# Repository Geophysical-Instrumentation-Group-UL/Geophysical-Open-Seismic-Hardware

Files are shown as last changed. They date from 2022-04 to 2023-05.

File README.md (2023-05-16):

# Geophysical Open Seismic Hardware

The Geophysical Open Seismic Hardware initiative is brought to you by the Geophysical Instrumentation Group at Université Laval (GIGul) and is funded by the Fonds de Recherche du Québec- Nature et technologies (FRQNT). This open-hardware contribution provides Earth Scientists around the world with a reference design for multi-component borehole seismic array that can be deployed from a conventional wireline winch used in the mineral industry (1/8 single conductor armoured cable). This design is engineered around the Teensy 4.0 microcontroller board which is compatible with the Arduino ecosystem and will be familiar to engineers and tinkerers. Our design philosophy is to include easily sourced components as part of modules that can readily be modified for other geophysical acquisition projects.

This repository contains all the design files for the different printed circuit boards that are integrated in this modular design(PCB). The first module includes a 3 channel 24 bit ADC that can sample signals up to 32 kHz. The second module is a power supply module that is configured to condition the power used by downhole shuttle. We provide a KiCad version of these design files. In early 2022, we migrated the project from Altium to KiCad in order to meet the ethos of our project and allow more users to benefit from our developments. Here are images of the V2 prototype WorkerBoard as assembled in december 2022. 

 Details about specific aspects of the project can be found on in the doc repository. For more information and questions please contact arnaud.mercier05@gmail.com or christian.dupuis@ggl.ulaval.ca.

 The hardware development is under the TAPR Open Hardware License, while the firmware is under the GNU General Public License V3. License files are within respective directory.

Addition of November 2022 : 
A basic GUI is now available. This first version allows the user to configure and control the system with 3 shuttles. It also have a display window to anayse the individual shots as well as the stacked trace.

The article titled ``Geophysical Open Seismic Hardware: Design of a Vertical Seismic Profiling Instrument'' documents the performance and the first field validation of the prototype : https://openhardware.metajnl.com/articles/10.5334/joh.50

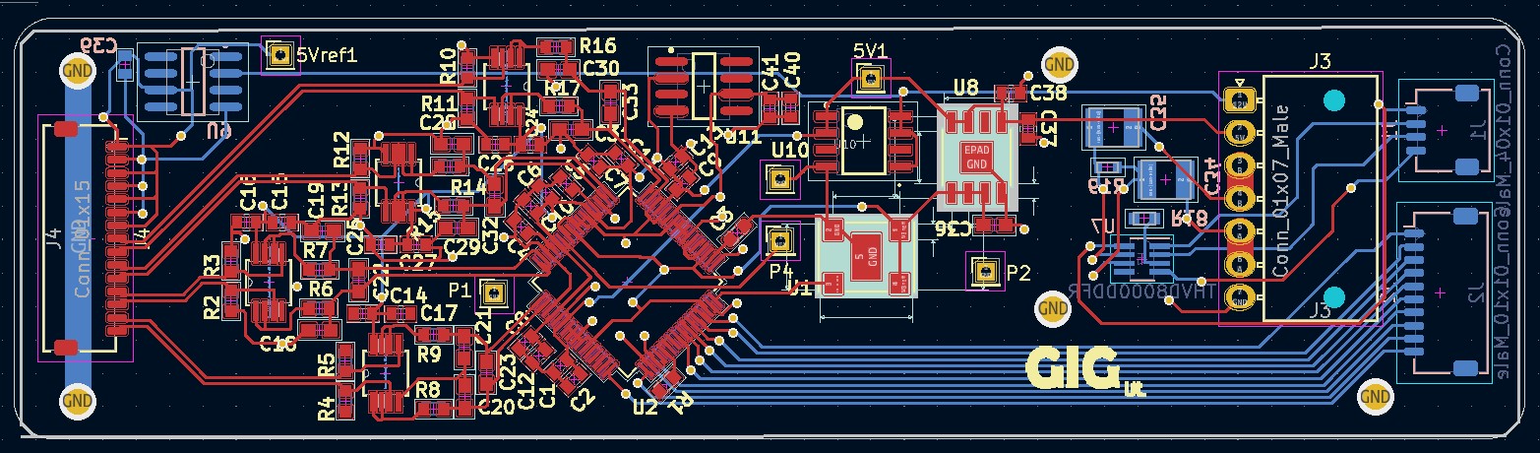
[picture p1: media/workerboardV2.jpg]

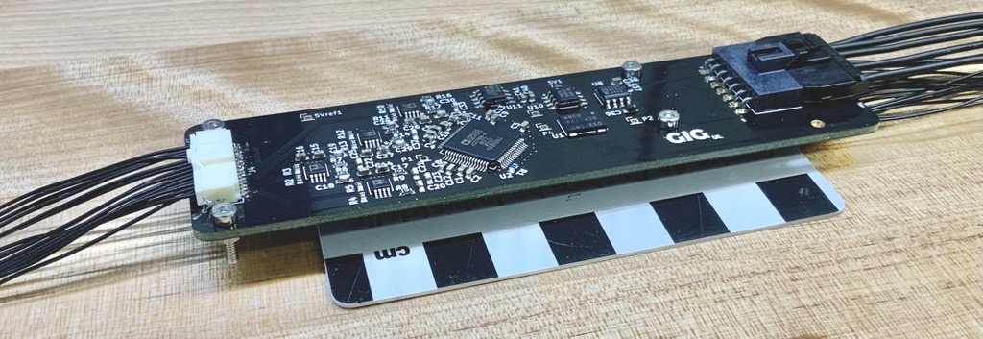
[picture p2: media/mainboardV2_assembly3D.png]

GUI

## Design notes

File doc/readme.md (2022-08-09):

GiGUL

# Welcome to the Geophysical Open Seismic Hardware documentation!
In this directory you will find details about the Geophysical Open Seismic Hardware project goals, design guidelines, assembly instruction and current stage of development. This repo is hosting the modifiable hardware files, assembly instruction and software required to operate the tools.

# What

 The Geophysical Open Seismic Hardware initiative is to design an open source VSP tool that is modular and can be reused or adapted by other research group for their purposes.  This contribution presents our first geophysical open-hardware contribution. We have developed a rugged and versatile 24-bit geophysical logger. The control and synchronization of the acquisition system is engineered around Arduino compatible microcontrollers that are open-source. This provides an intuitive and vibrant development community. A frequency modulated communication protocol allows us to communicate data efficiently and send power over a single conductor wireline. This modular geophysical logger can easily be reconfigured to be used with multiple sensors. The first use case of this logger is a Vertical Seismic Profiling tool chain. The novel design reduces the overall cost and size, which facilitates the deployment of more channels and in configurations that are not feasible with current commercial equipment. In particular the system in composed of :

- Analog accelerometer from Silicon Design (SI1521L)
- AD7768 multi-channel Delta-Sigma 24 bits ADC
- THVD8000 Frequency modulated RS-485
- Teensy 4.0 MC

# Overview

The system is based on a leader/worker arrangement. The leader (master) unit uphole is connected directly via USB to the PC. This leader unit is the same as the worker unit without the power supply and sensor modules. There are multiple Workers (shuttles) but only one leader uphole. DC voltage is applied on the A and B line which is used to power up the worker units. Each worker is in a pressure housing to be able to sustain borehole conditions. At the time being, the pressure housing is still in development.

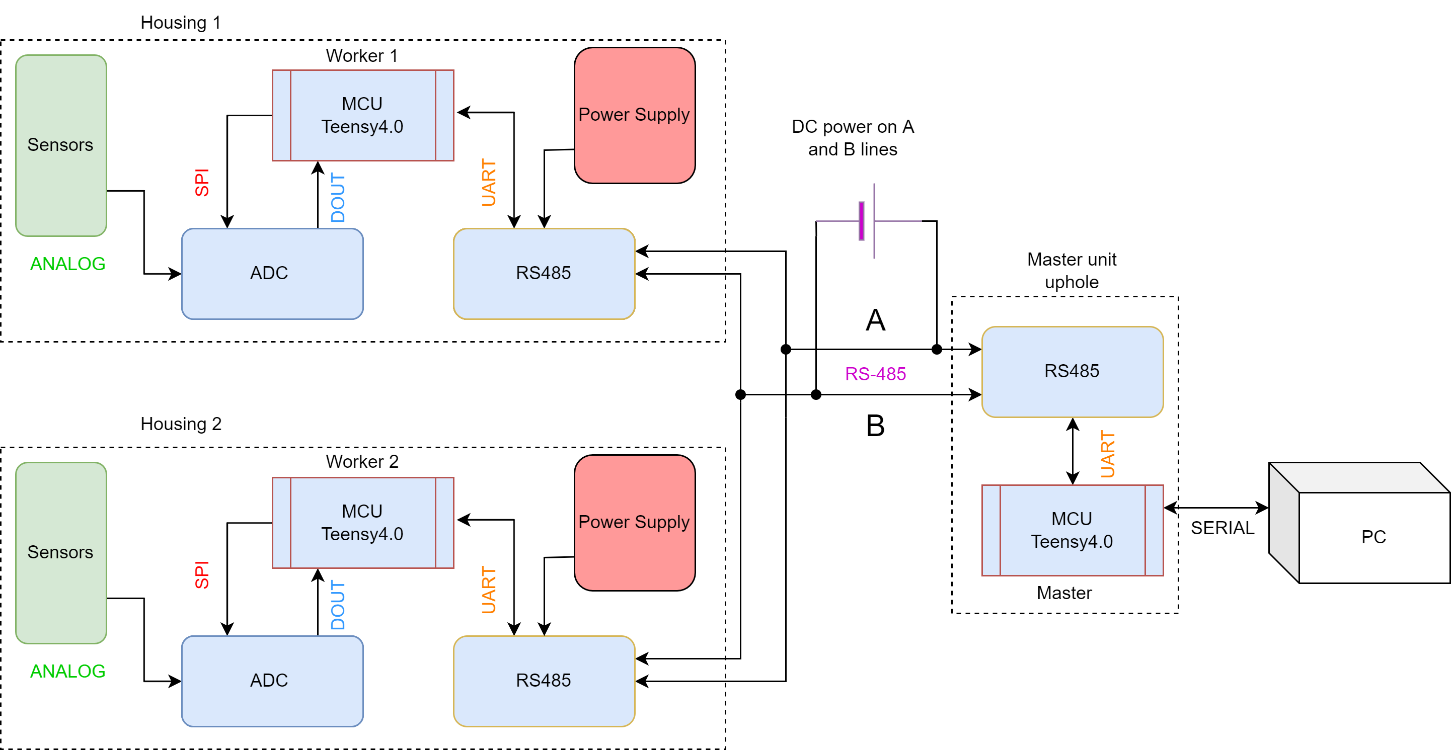
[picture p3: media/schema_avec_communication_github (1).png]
Scheme


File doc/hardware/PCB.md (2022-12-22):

# Printed circuit board details

----

## Main board (ADC_RS)

The components have been divided on 3 different printed circuit boards (PCB). The main board contains the ADC, the MCU and the communication module. This board has 4 layers in order to reduce its size as much as possible and to ensure a decoupling between the digital signals, the analog signals and the power supply. Its dimensions of 40 by 160 mm respects the objective of a diameter less than 46 mm. The Altium version contains micro-vias, which is more costly to produce. This version is deprecated and is present here only for reference. The active board is the KiCad version, which doesn't have micro-vias.

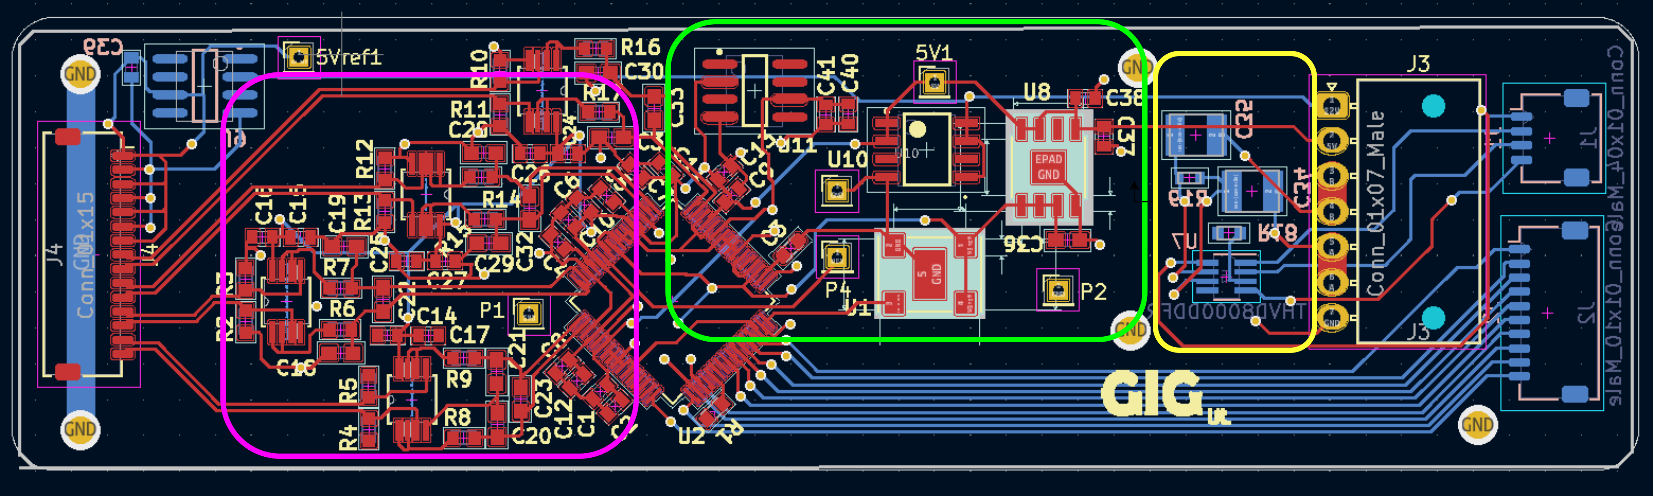
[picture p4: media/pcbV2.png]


### ADC drivers (pink)

Those are 2 channels amplifiers with unity gain to drive the ADC analog inputs. They are ADA4841-2 from Analog Device. The output of a sensor has 2 signals. Both signal are conditioned by an amplifier before going to the ADC. The design of this amplification stage is based on the application note https://www.analog.com/media/en/technical-documentation/application-notes/AN-1384.pdf.

### Voltage regulator (green)

4 different voltage regulator are used on this board. The 4.096 V is used as a reference for the ADC. The 3.3 power up the clock and reference the ADC. The 5Vref is the reference for the sensors and it is a high precision voltage regulator while the 5V is used to power up the ADC and other component, he can produce higher current than the 5Vref. 

### RS-485 (Yellow)

The THVD8000 is responsible of transforming the UART data to a frequency modulated RS-485 signal that is send on the A and B line. The carrier frequency is set by the R22 resistors. Values of resistor can be found in the THVD8000 [datasheet](https://www.ti.com/product/THVD8000?utm_source=google&utm_medium=cpc&utm_campaign=asc-int-null-prodfolderdynamic-cpc-pf-google-wwe&utm_content=prodfolddynamic&ds_k=DYNAMIC+SEARCH+ADS&DCM=yes&gclid=Cj0KCQjwof6WBhD4ARIsAOi65ajVA_-4Qv5Z8-NflDabHUv2FtYJd0RHMERMfylwqK505uBJHmn_EZ0aAl1MEALw_wcB&gclsrc=aw.ds). The choice of the decoupling capacitor is based on the application note here [THVD8000 design guide](https://www.ti.com/lit/an/slla496a/slla496a.pdf?ts=1658843537116&ref_url=https%253A%252F%252Fwww.ti.com%252Fproduct%252FTHVD8000%253Futm_source%253Dgoogle%2526utm_medium%253Dcpc%2526utm_campaign%253Dasc-int-null-prodfolderdynamic-cpc-pf-google-wwe%2526utm_content%253Dprodfolddynamic%2526ds_k%253DDYNAMIC%2BSEARCH%2BADS%2526DCM%253Dyes%2526gclid%253DCj0KCQjwof6WBhD4ARIsAOi65ajVA_-4Qv5Z8-NflDabHUv2FtYJd0RHMERMfylwqK505uBJHmn_EZ0aAl1MEALw_wcB%2526gclsrc%253Daw.ds).

### Connectors 

J1 is dedicated to the communication chip. Theses wire have to be connected to the chosen MCU. J2 is a 10 pin connector dedicated to the configuration and communication with the ADC. J3 is a 7 pin high power connector used by the A,B and 12V lines. Finally, the J4 15 pin connector is used to drive and collect the signals from 4 analog differential sensors.

## Power supply

The power supply and its component are built into a separate 40 by 85 mm PCB. This way, switching noise cannot affect the precision components of the main board. The design is based on the [DC2895A](https://www.analog.com/en/design-center/evaluation-hardware-and-software/evaluation-boards-kits/dc2895a.html#eb-overview) demo board. On one side the A and B line enters and goes thru the inductor to filter out the high frequency.  Since the cable is expected to have a high capacitance (140 microF), turning on the power supply can create a  current surge. The added 100 Ohms resistor (R5) allows to reduce the current spike when turning on the power supply. The mode header is used to set the operating mode for the output of the power supply. Burst mode is the default since it draws less current.

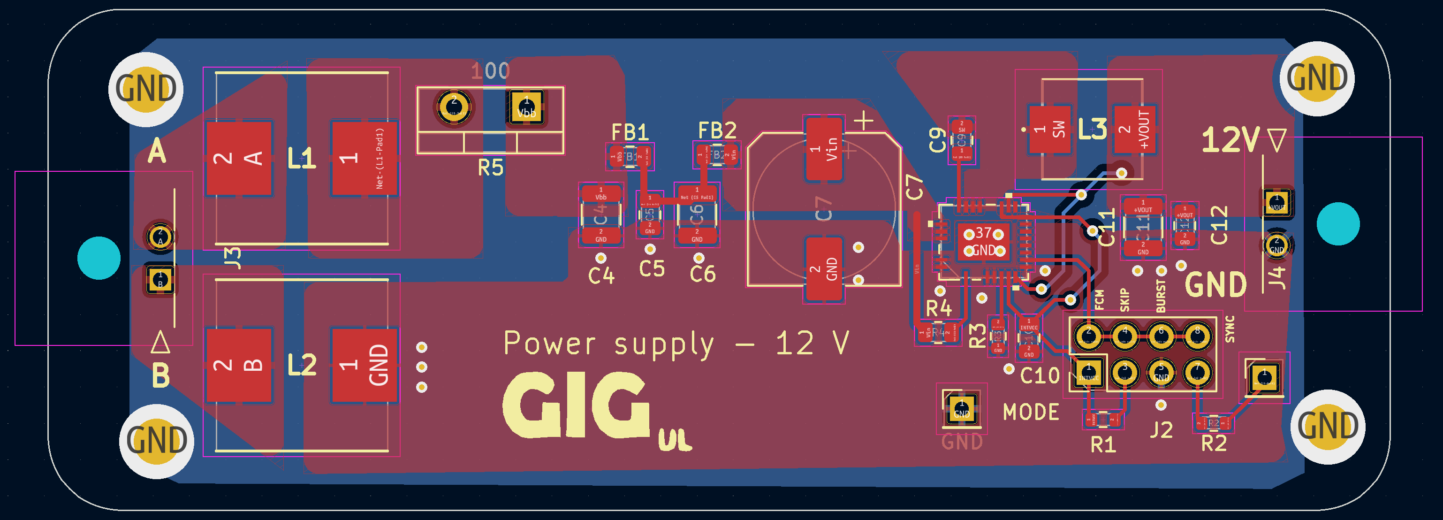
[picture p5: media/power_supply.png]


## Sensors

The sensors are assembled on miniature PCBs in order to facilitate the assembly on a mount with the desired geometry.  Wires are soldered directly into the sensor boards. These wires are linked to the main board by a locking clip connector to ensure proper contact The PCB follows the connection proposed in the sensor datasheet ([si1521L](https://www.silicondesigns.com/_files/ugd/3fcdcf_d6eb801b372f408bbba8180fd1f07cc7.pdf)). 

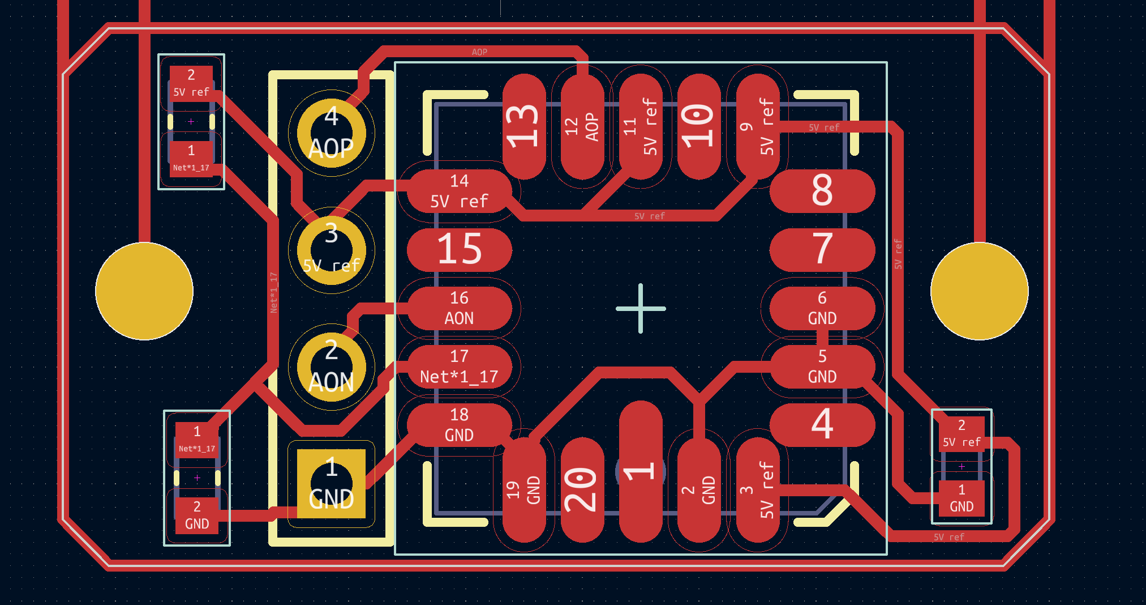
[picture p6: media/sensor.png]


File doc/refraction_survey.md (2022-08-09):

# Refraction survey

---

Here is the details about the refraction survey from the article. All the 3D files have been developed in CREO and are available in the 3D_files directory.

## Goals

- Compare our system with the well proven *Geode* from geometrics (first arrivals and complete seismograph)
- Test the custom 3 components sensor package

## Integration of the electronics

### Sensor package

The SI 1521L are soldered on the sensor board and jumper wires are soldered to the PCB. A 3D printed box with tapered insert allow to fix the PCB in an orthogonal arrangement. Every board are connected to a wall mount DB15 connector.

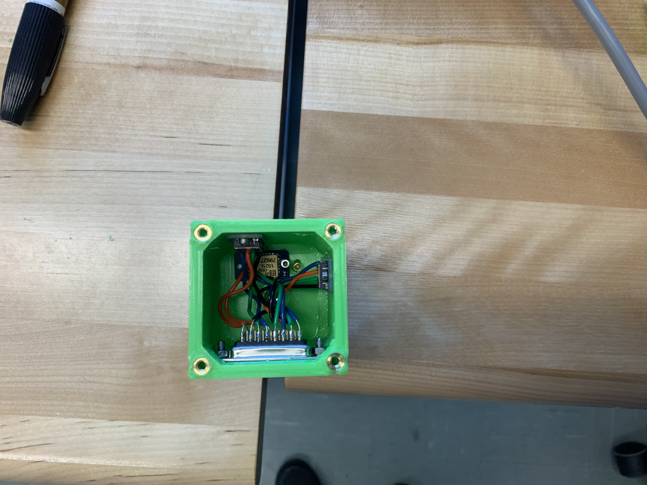
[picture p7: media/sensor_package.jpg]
sensors


### Main board and power supply

The main board and the power supply board were integrated onto an 3D printed frame via screws. On one end of the frame is a custom expander plug mechanism and on the other end a printed TPU (flexible) ring. These allow to slide the frame inside an 2 inch aluminium tube and lock the frame so it doesn't move. A custom cable is assemble based on a DB15 cable. Wires for the sensor package that come from the main board are soldered into the pre-assemble DB15 cable and wrapped around heat-shrink.

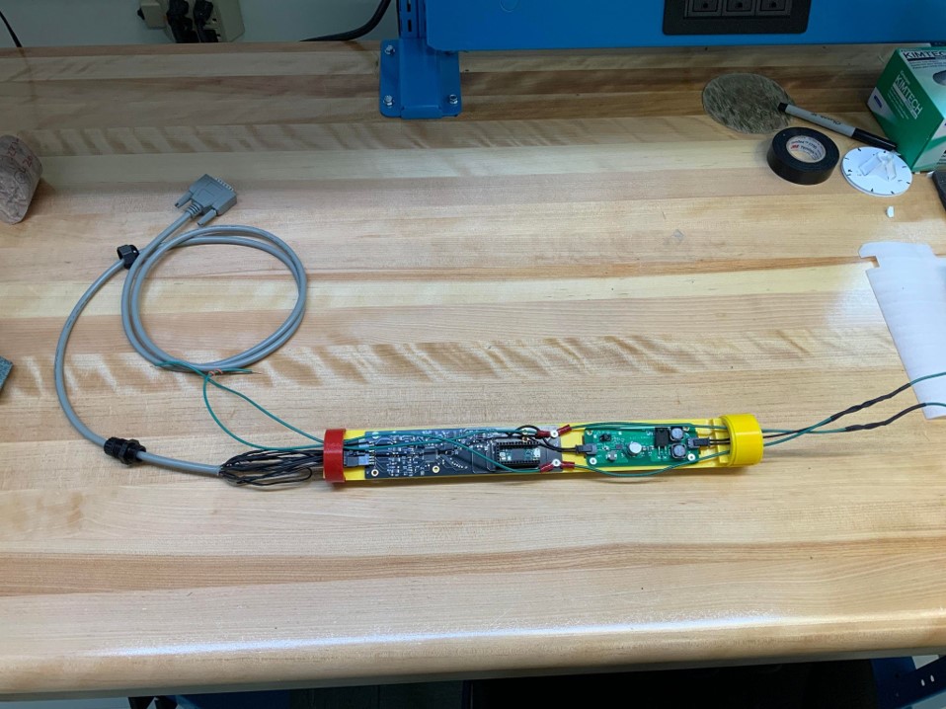
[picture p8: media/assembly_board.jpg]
assembly


### End cap

A custom end cap is designed and 3D printed. This cap has some threaded insert so it can be fix by a screw through the tube wall. These cap have a cavity for a cable gland for the DB15 cable and for the coax wall mount connector.

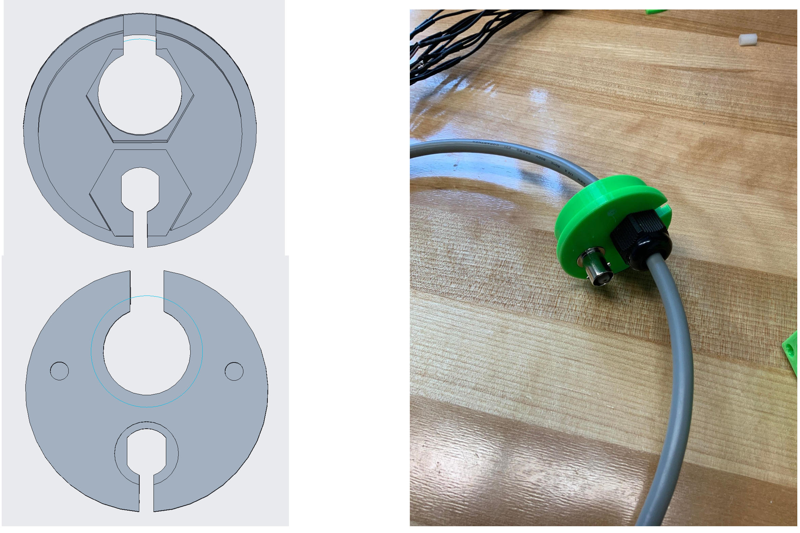
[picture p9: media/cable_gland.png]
gland

coax

### Master box

The master unit is bolted into a simple 3D printed box with a removable cover. The box has a wall mount coax connector and a slid to allow the passage of the USB cable. Banana jack are included to connect the external power supply. Wires for the trigger are accessed from a hole in the box cover.

box

### Custom trigger

A custom trigger system composed of a piezo-electric ([Sparkfun](https://www.sparkfun.com/products/10293)) element is mounted onto a sledgehammer. The mount is 3D printed and is divided in 3 main parts:

- 2 pieces clamp in rigid plastic (CPE)
- 2 half-circle TPU ring that provides damping and reduce stress on the CPE plastic
- 1 TPU top cap to keep the piezo in place

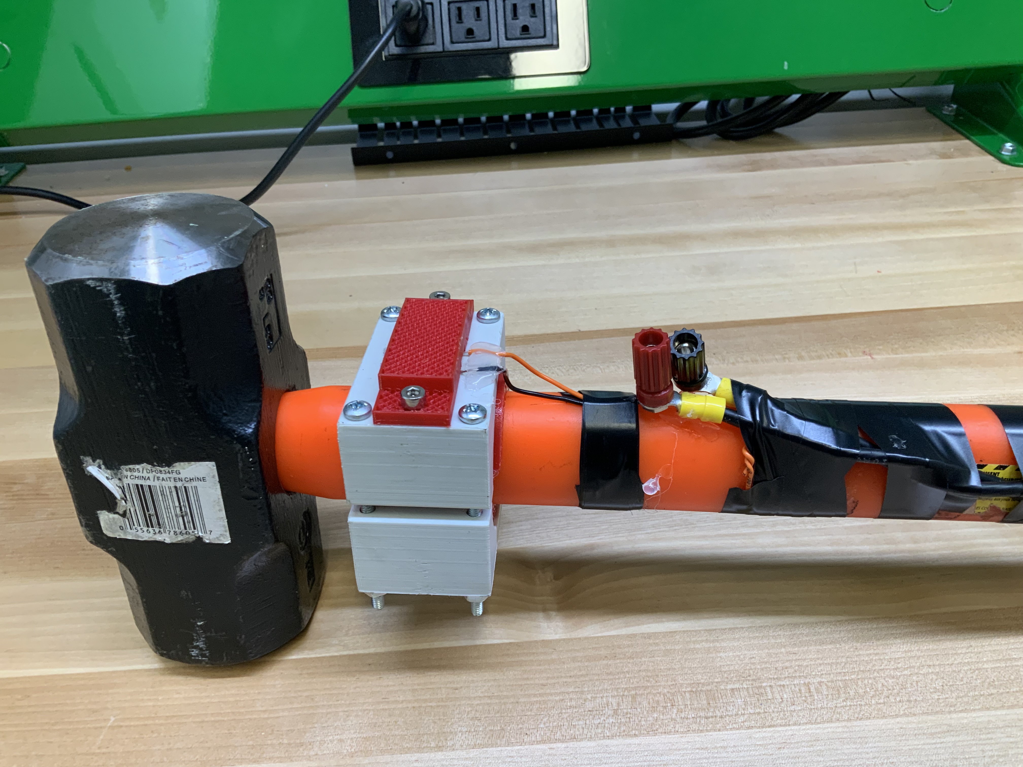
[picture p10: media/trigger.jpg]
trigger


## Material used

- Voltage source (HMP4040 from Rhode and Schwarz)
- Generator to power the voltage source
- Laptop with the custom software for the tool
- Sledgehammer and metal plate
- Measuring tape
- Geode from geometrics and associated cables
- Laptop with proper geometrics software
- 12 V battery
- Geophones (ION 28 Hz)

## Geometry

See images in the article.

## Data

Raw data are stored in .txt files and are available on request.

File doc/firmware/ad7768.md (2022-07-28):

**Homemade librairy to configure ad7768 with Arduino SPI**

This librairy is adapted from the original ad7768 librairy from [Analog device ad7768](https://github.com/analogdevicesinc/no-OS/blob/master/drivers/adc/ad7768/ad7768.c). It implements the same logic but adapted with he Arduino SPI function.

All functions are based on a _ad7768_chip_ object:

    typedef struct {
        ad7768_chip_select_pin chipSelectPin = 10; //teensy 4.0 CS pin
        ad7768_power_mode	power_mode;
        ad7768_mclk_div		mclk_div;
        ad7768_dclk_div		dclk_div;
        ad7768_dec_rate		dec_rate;
        ad7768_filt_type	filt_type;
    } ad7768_chip;

This object contains a list parameters of a type enum. This makes it easier and cleaner when configuring a new chip. For example, in the declaration of a new chip, one can decide to set the power mode to only theses values:

    typedef enum {
        AD7768_ECO = 0,
        AD7768_MEDIAN = 2,
        AD7768_FAST = 3,
    } ad7768_power_mode;

Some functions have a mask input parameter. This allows to write in only a specific part of a registry without changing the already in place values. The function _print_config_ has a stream input parameter. This allows to print the configurations in a specific Serial port. 

A list of the registry address is define in the .h file. Those are taken from the datasheet. This librairy is dependant on the Arduino SPI librairy and Stream librairy only.

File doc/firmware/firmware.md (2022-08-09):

# Firmware

In this page you will find details about the Geophysical Open Seismic Hardware firmware, design guidelines and current stage of development. The details about the librairy used in the projects can be found in the command and ad7768 files.

# Design guidelines

This basic software is the first prototype of the control software. Only the essentials functions are implemented. This software looks at doing 2 things in particular:

- Ease of use and high-level function to operate the system [main.py and mainLeader].
- High-speed acquisition of seismic signal from the ADC (32 kHz) [mainWorker].

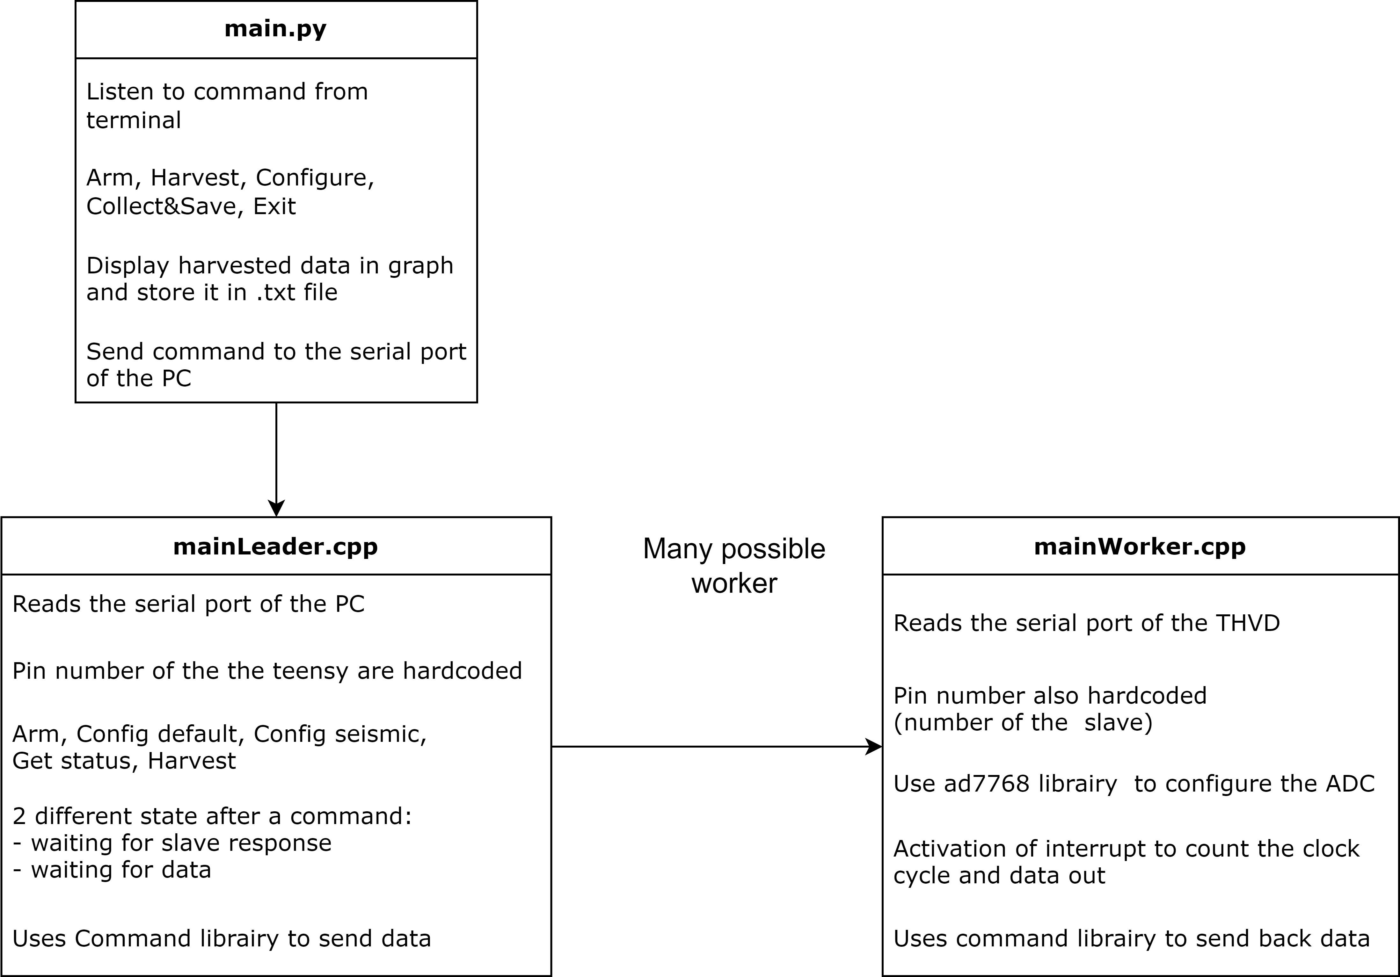
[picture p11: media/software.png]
Software


# Principal elements in main scripts:

## main.py

This script runs on the PC used for the acquisition. It must be launched in the terminal once the leader unit is connect by USB. This script allow the user to enter high level command to perform a basic survey.

- Read the input of the terminal (the serial port and baud rate must be specified, 115200 by default).
- Transform the data from 24 bits to voltage. The values are hardcoded.
- Plot the results of the harvested data (only 3 worker for now).
  The X is the value of the worker you wish to harvest.
- Typical use case:
  - Enter the sampling rate and duration in the terminal.
  - Create a new stack.
  - Use of arm and collect function after each shot (shot count will appear).
  - Use of the show stack function to display individual shots and stacked traces.
  - Create a new stack and carry on.

## mainLeader.cpp

This script runs on the leader MCU (Teensy 4.0). The MCU are programmed from the PlatformIO extension in Visual Studio code.

- Read the serial from PC and read the command (Uses the by default serial port to PC and a specific serial port to the RS485 chip).
 - If the arm command is detect the trigger interrupt is activated.
 - If the trigger is detected, a signal is sent to the workers and the trigerred state is turned off.
- If the harvest data command is detected the flag waitForData is activated.

The script uses the functions of the _command_ librairy to communicate with the workers. When the leader waits for a worker response the function _readCommand_ of the _command_ librairy is used to detect the incoming command type from the worker.

## mainWorker.cpp

This script runs on every worker MCU (Teensy 4.0). The MCU are programmed from the PlatformIO extension in Visual Studio code. Each worker must be assigned a unique workerID. This will allow the leader unit to communicate with a single worker at the time. In the future, the workerID attribution would likely be automated.

- Read the serial port of the RS485 communication line.
- Sort the command type with _readCommand_ function.
- Configures the adc with the specified configuration.
- If the arm command is detected the interrupt for the clock and for the drdy (dataready from the adc) is activated. The status ready to trig is then activated so the serial port is checked for this particular command.
- Once the ready to trig flag is true, the scripts only waits for a 't' on the serial port. When it sees it, it activated the triggered_state to true and the acquisition time is set to 0. This previous block of code is under a nointerrupt condition.
- When a drdy interrupt is detected the clck count is set to 0.
- the read_ISR function is called every clck count the register the data in a pre defined vector (binary data). The data is read on 3 different pins at 4 MHz. This is why we need a fast MCU (the time required to change pins is long...). Alternatively, one could decide to output every channel of the ADC on the same pins, one after the other. This would mean the MCU as only to read data on a single pin, which is faster.
- At the 33 clck count the data_packet_ready flag is activated and the data is transformed form bit to integer.
- The interrupt are then disable and the triggered status and ready to trig status are set to false.

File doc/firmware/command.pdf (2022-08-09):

This homemade librairy implements hihg level functions to operate the open-seismic harware

All functions needs a stream object, wich is the serial port you want to use to send command. All function use a command object to transfer data:

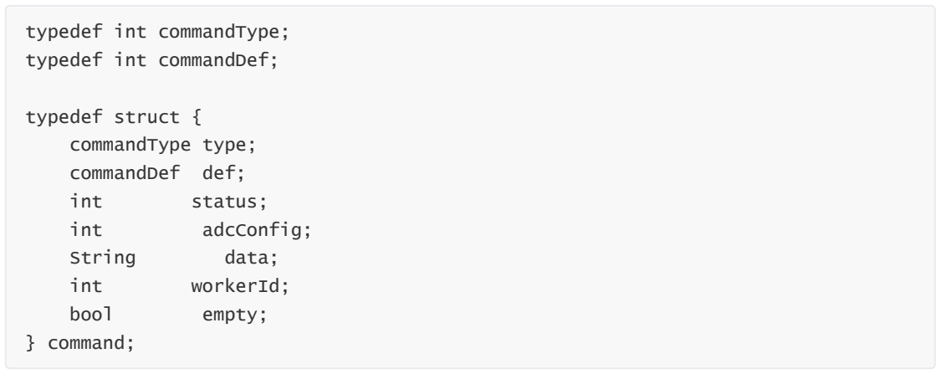
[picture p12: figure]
typedef int commandType;; typedef int commandDef;; typedef struct {; commandType type; commandDef def;; int; status;; adcConfig;; String; data;; workerId;; bool; empty;; } command;

This allows to have different command object depending on the communication needs.

The buildAndSendCommand function send all the parameters in the command struct object with a letters before each parameter. This makes it easy to decode the information in the readCommand function.
When the leader wants to harvest the data from a worker the it send a command asking for data. The workers writes the data directly into the serial port while the leader is ready to listen.

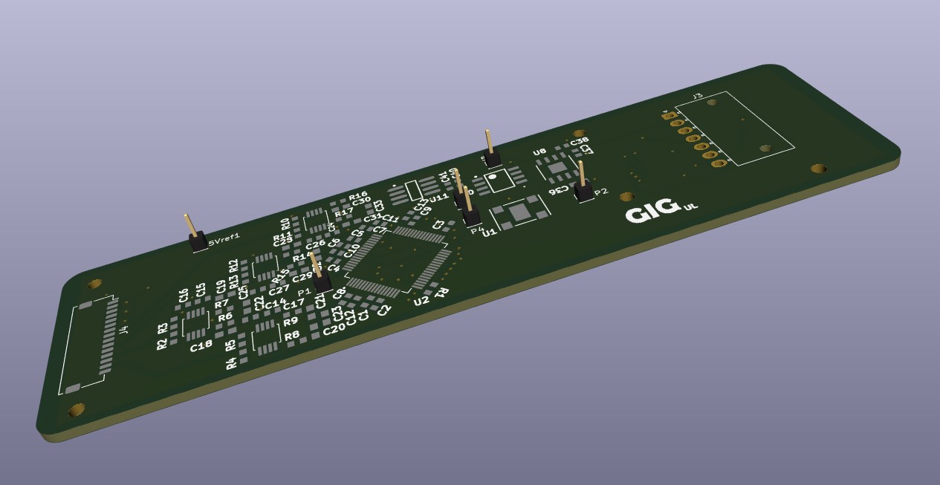
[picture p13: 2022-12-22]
media/workerboardV2_3D.jpg

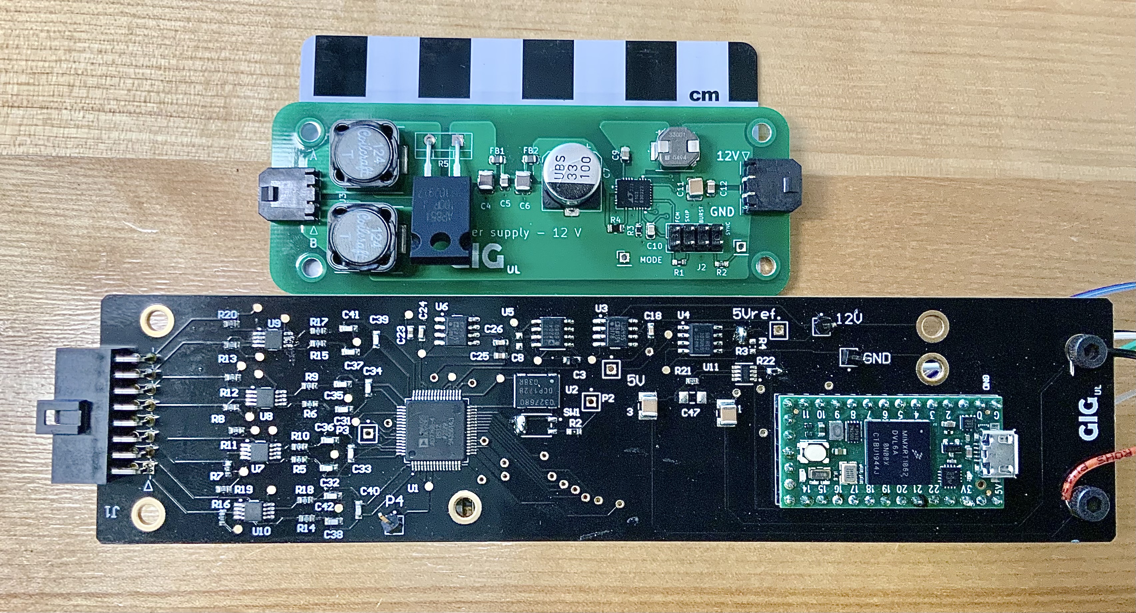
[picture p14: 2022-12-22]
media/mainboardV1+power_supply.jpg

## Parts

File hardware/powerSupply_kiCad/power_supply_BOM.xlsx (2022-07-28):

Item | Quantity | Designator | Manufacturer_Name | Comment | Manufacturer Part Number | Mouser Part Number | Digikey Part Number | Description | Footprint
1 | 2 | C4, C6 | Taiyo Yuden Co., Ltd. | 4.7 uF - 100V | HMK325C7475KN-TE |  | 587-5038-1-ND | CAP CER 4.7UF 100V X7S 1210 | C_1210_3225Metric
2 | 1 | C5 | Taiyo Yuden Co., Ltd. | 0.22 uF - 100V | HMK212B7224KG-T |  | 587-2087-1-ND | CAP CER 0.22UF 100V X7R 0805 | C_0805_2012Metric
3 | 1 | C7 | Vishay | 33uF - 100V | 100SEV33M10X10.5 |  | 1189-3062-1-ND | CAP ALUM 33UF 20% 100V SMD | CP_Elec_10x10.5
4 | 1 | C9 | Murata | 0.1 uF - 100V | GRM21BR72A104KAC4L |  | 490-12005-1-ND | CAP CER 0.1UF 100V X7R 0805 | C_0805_2012Metric
5 | 1 | C10 | Kyocera AVX | 1 uF - 16V | 0805YC105KAT2A |  | 478-5034-1-ND | CAP CER 1UF 16V X7R 0805 | C_0805_2012Metric
6 | 1 | C11 | Murata | 22 uF - 16V | GRM32ER71C226KEA8L |  | 490-5890-1-ND | CAP CER 22UF 16V X7R 1210 | C_1210_3225Metric
7 | 1 | C12 | Samsung Electro-Mechanics | 1 uF - 50V | CL21B105KBFNNNG |  | 1276-6470-1-ND | CAP CER 1UF 50V X7R 0805 | C_0805_2012Metric
8 | 2 | FB1, FB2 | Würth Elecktronik | FerriteBead | 782853131 |  | 732-782853131CT-ND | WE-CBA SMT EMI SUPPRESSION FERRI | C_0805_2012Metric
9 | 1 | IC1 | Analog Devices Inc. | LT7101EUHE-PBF | LT7101EUHE#PBF |  | 505-LT7101EUHE#PBF-ND | Buck Switching Regulator IC Positive Adjustable 1V 1 Output 1A 36-WFQFN, 26 Leads, Exposed Pad | LT7101EUHE-PBF
10 | 1 | J1 |  | CLCK | 68000-201HLF |  | 609-68000-201HLF-ND | Through hole straight pin header, 1x01, 2.54mm pitch, single row | PinHeader_1x01_P2.54mm_Vertical
11 | 1 | J2 |  | MODE | 68000-201HLF |  | 609-68000-201HLF-ND | Through hole straight pin header, 2x04, 2.54mm pitch, double rows | PinHeader_2x04_P2.54mm_Vertical
12 | 2 | J3, J4 | Molex | 436500201 | 436500201 |  | WM1865-ND | CONN HEADER R/A 2POS 3MM | 436500201
13 | 1 | J5 |  | GND | 68000-201HLF |  | 609-68000-201HLF-ND | Through hole straight pin header, 1x01, 2.54mm pitch, single row | PinHeader_1x01_P2.54mm_Vertical
14 | 2 | L1, L2 | Coilcraft | 120 uH - 1.9A | MSS1278-124KLD | 994-MSS1278-124KLD |  | MSS1278-124KLD | INDPM120120X805N
15 | 1 | L3 | TDK | 33 uH | SPM7054VT-330M-D |  | 445-181516-1-ND | FIXED IND 33UH 3.4A 107.47 MOHM | SPM7054VT
16 | 1 | R1 | Vishay | 100 k | CRCW0603100KDHEAP |  | 541-100KAYCT-ND | RES SMD 100K OHM 0.5% 1/10W 0603 | R_0603_1608Metric
17 | 1 | R2 | Stackpole Electronics Inc | 1 k | RMCF0603FG1K00 |  | RMCF0603FG1K00CT-ND | RES 1K OHM 1% 1/10W 0603 | R_0603_1608Metric
18 | 1 | R3 | Stackpole Electronics Inc | 9.31 k | CRCW06039K31FKEA |  | 541-9.31KHCT-ND | RES SMD 9.31K OHM 1% 1/10W 0603 | R_0603_1608Metric
19 | 1 | R4 | Vishay | 10 M | RCS080510M0FKEA |  | 541-2854-1-ND | RES SMD 10M OHM 1% 0.4W 0805 | R_0805_2012Metric
20 | 1 | R5 | Ohmite | 100 | AP851 100R J |  | AP851100RJ-ND | RES 100 OHM 5% 50W TO220 | TO-220-2_Vertical

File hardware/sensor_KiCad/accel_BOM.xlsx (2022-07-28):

Item | Quantity | Designator | Manufacturer_Name | Comment | Manufacturer Part Number | Mouser Part Number | Digikey Part Number | Description | Footprint
1 | 1 |  | Kyocera AVX | 0.1uF | 06033D104KAT2A | 581-06033D104K |  | Cap Ceramic 0.1uF 25V X5R 10% SMD 0603 85ÂÂŽ T/R | CAPC1608X90N
2 | 4 |  | Amphenol ICC (FCI) | Header 4 | 68000-201HLF |  | 609-68000-201HLF-ND | Header, 4-Pin | HDR1X4
3 | 1 |  | Silicon Design | SI1521L | SI1521L |  |  | Silicon Design SI-1521L-002 +- 2g LCC-20 Surface mount accelerometer | LCC127P889X889X254-20N
4 | 2 |  | YAEGO | 2k | RC0603DR-072KL |  | 13-RC0603DR-072KLTR-ND | 2 kOhms ±0.5% 0.1W, 1/10W Chip Resistor 0603 (1608 Metric) Moisture Resistant Thick Film | RESC1608X55N

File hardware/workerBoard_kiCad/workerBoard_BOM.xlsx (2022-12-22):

Id | Designator | Package | Quantity | Designation
1 | C29,C18,C20,C31,C28,C19,C21,C30 | CAPC1608X90 | 8 | 120pF
2 | R11,R4,R13,R10,R2,R5,R3,R12 | RESC1608X55N | 8 | 1M
3 | C33,C23,C32,C22 | CAPC1608X90 | 4 | 330pF
4 | P2,5V1,P1,5Vref1,P4,P3 | PinHeader_1x01_P2.00mm_Vertical | 6 | Plug
5 | C40,C1,C6,C26,C7,C37,C17,C4,C27,C16,C8,C5,C9 | CAPC1608X90N | 13 | 1u
6 | R7,R17,R15,R6,R8,R9,R16,R14 | RESC1608X55N | 8 | 33
7 | C2,C14,C41,C24,C25,C10,C12,C11,C15,C13,C38,C39 | CAPC1608X90N | 12 | 0.1uF
8 | U11 | ADI-R-8_M | 1 | ADR4540BRZ
9 | J4 | Molex_Pico-Clasp_202396-1507_1x15-1MP_P1.00mm_Horizontal | 1 | Conn_01x15
10 | C36 | CAPC1608X90 | 1 | 2.2uF
11 | U6,U4,U5,U3 | ADA4841-2YRMZ | 4 | RM_8_ADI
12 | U8 | SOIC_08_EP_3P9X4P9_ADI | 1 | ADP7118ARDZ-3.3-R7
13 | C3 | CAPC1608X9N | 1 | 10uF
14 | U10 | D0008A_M | 1 | REG103UA-5
15 | R1 | RESC1508X55N | 1 | 100
16 | U2 | QFP50P1200X1200X160-64N | 1 | AD7768-4BSTZ
17 | U1 | DFN4_7X5_MCH | 1 | DSC1001AI2-032.7680
18 | J3 | Molex_Nano-Fit_105313-xx07_1x07_P2.50mm_Horizontal | 1 | Conn_01x07_Male
19 | C35,C34 | CAPC3326X280N | 2 | 0.47uF-250V
20 | U9 | ADI-R-8_M | 1 | ADR435BRZ
21 | R18 | RESC1608X55N | 1 | 1.5k
22 | J1 | Molex_Pico-Clasp_202396-0407_1x04-1MP_P1.00mm_Horizontal | 1 | Conn_01x04_Male
23 | J2 | Molex_Pico-Clasp_202396-1007_1x10-1MP_P1.00mm_Horizontal | 1 | Conn_01x10_Male
24 | U7 | SOT-23-8_Handsoldering | 1 | THVD8000DDFR
25 | R19 | RES_ERA3AEB121V | 1 | 120

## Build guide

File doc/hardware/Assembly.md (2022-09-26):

# Assembly

----

The assembly is done is 2 parts. The material needed is:

- Reflow oven or hot air gun for soldering to solder SMD parts
- Soldering iron to solder through hole parts
- Multimeter
- Osilloscope
- Precision tweezers
- Microscope (optionnal)

Firstly the SMD components must be soldered. The use of a stencil is highly recommended. The stencil can be ordered with the boards. Solder paste is then applied to all the board. Components are then placed according to their position (referred in the BOM file). At this point either a hot air gun or a appropriate oven can be use to reflow the solder paste. We use the AS-5010 oven from smtMAX with a specific reflow profile shown on the figure below.

Secondly, the through holes parts can be soldered with a classic soldering iron. Care must be taken to not overheat SMD component.

A video of the assembly of the worker board is available in the media directory. The assembly process is the same for the sensor and power supply board.

it is recommended to check every connection with a multimeter to ensure no shorts remains after the SMD soldering process. More secifically, here is a few verification that could be made to ensure proper working boards.

-  Make sure all planes have infinite impendance (5V, GND, TOP and BOTTOM)
-  Very large impedance between the differential channel of the input of the op-amp (see pink section of the PCB.pdf documentation file)
-  No shorts between the all the adjacent pins of the ad7768
-  No shorts between the A and B line

Once 12V is applied to the 12V pin, differents verification can be made with a multimeter and an oscillioscope.

- Make sure the power pins ouput the prescribed voltage (4.096V, 5V and 5V ref, 3.3V), see green section in the PCB.pdf documentation file
- With an oscilloscope, make sure the DCLK pins of the ADC outputs a clock signal at 4MHz
- Make sure the output of the external clock (U2) outputs a signal at 32.8 MHz

### smtMAX oven used

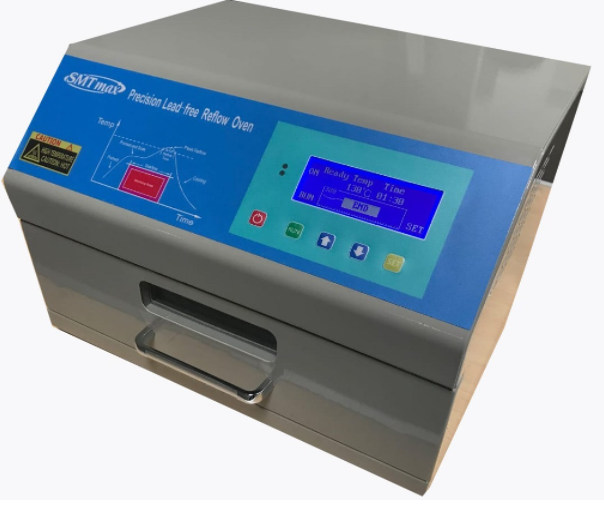
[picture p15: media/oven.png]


### Reflow profile used

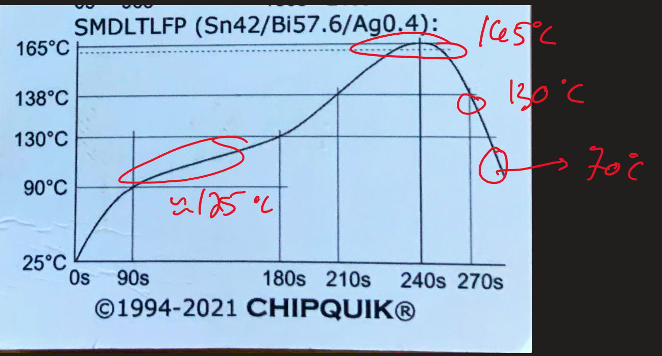
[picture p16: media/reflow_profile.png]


### Stencil used to apply the solder paste

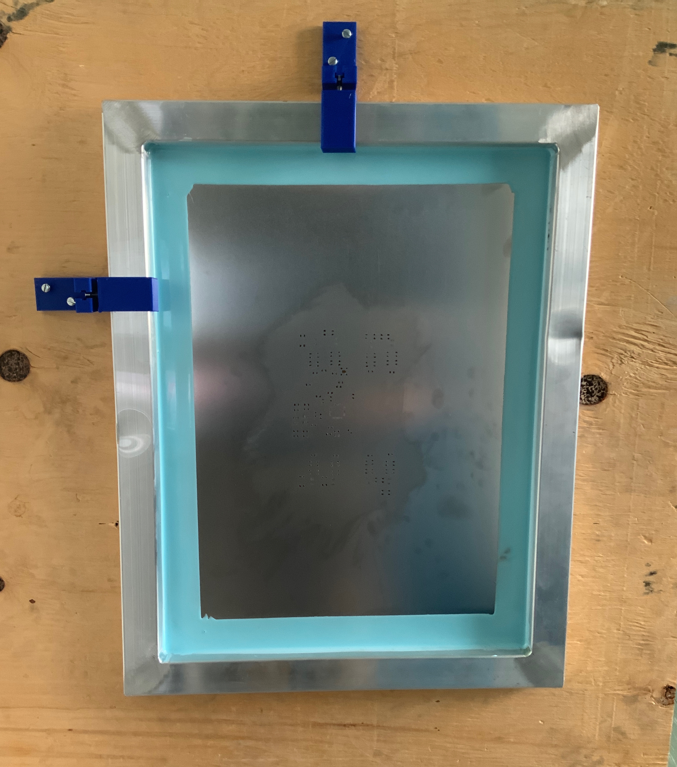
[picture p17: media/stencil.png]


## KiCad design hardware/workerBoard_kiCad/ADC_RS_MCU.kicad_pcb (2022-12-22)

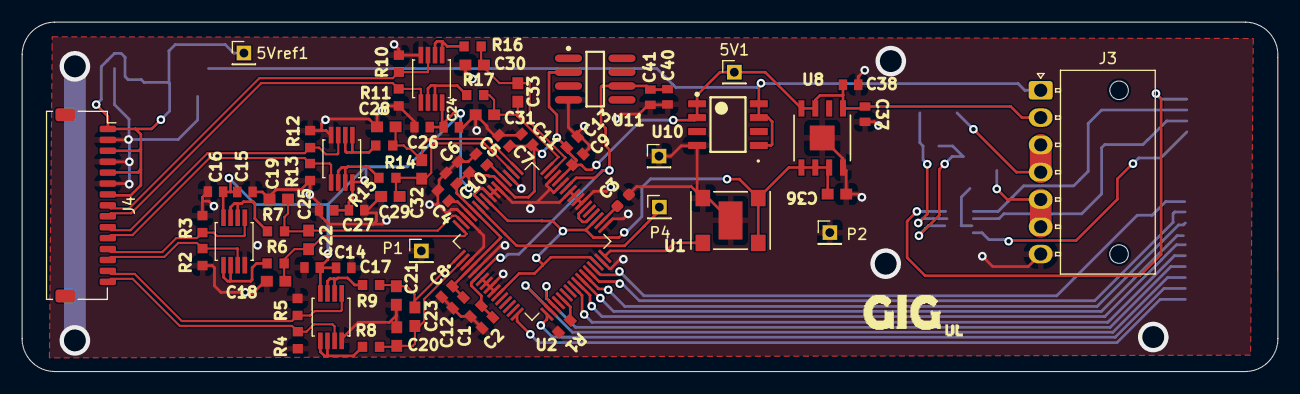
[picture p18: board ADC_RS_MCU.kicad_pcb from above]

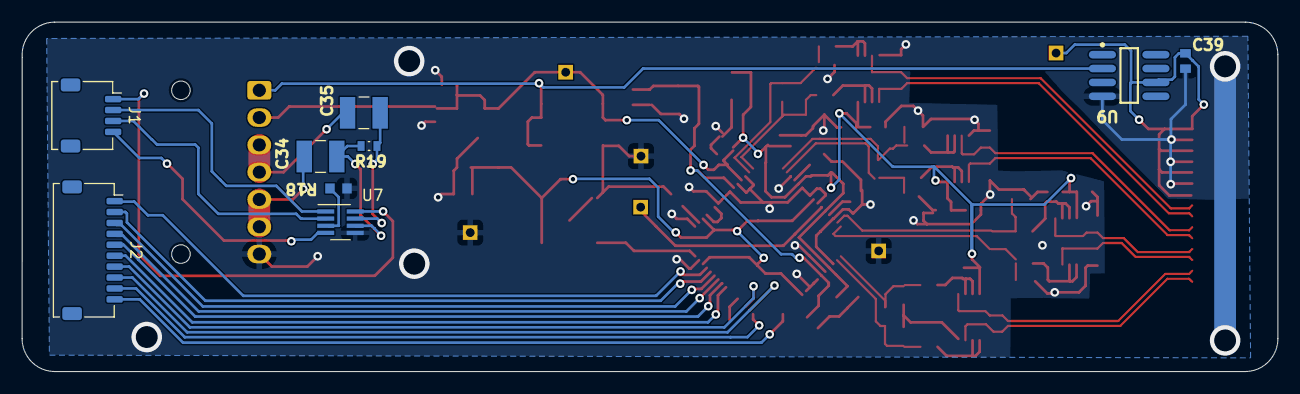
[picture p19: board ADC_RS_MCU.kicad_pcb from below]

Board: 4 copper layers, 115.0 x 32.0 mm, 81 parts (9 on the bottom side), 56 nets.

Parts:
5V1, 5Vref1: Plug; PinHeader_1x01_P2.00mm_Vertical
C1, C4, C5, C6, C7, C8, C9, C16, C17, C26, C27, C37, C40: 1u; CAPC1608X90N
C2, C10, C11, C12, C13, C14, C15, C24, C25, C38, C39, C41: 0.1uF; CAPC1608X90N
C3: 10uF; CAPC1608X9N
C18, C19, C20, C21, C28, C29, C30, C31: 120pF; CAPC1608X90
C22, C23, C32, C33: 330pF; CAPC1608X90
C34, C35: 0.47uF-250V; CAPC3326X280N
C36: 2.2uF; CAPC1608X90
J1: Conn_01x04_Male; Molex_Pico-Clasp_202396-0407_1x04-1MP_P1.00mm_Horizontal
J2: Conn_01x10_Male; Molex_Pico-Clasp_202396-1007_1x10-1MP_P1.00mm_Horizontal
J3: Conn_01x07_Male; Molex_Nano-Fit_105313-xx07_1x07_P2.50mm_Horizontal
J4: Conn_01x15; Molex_Pico-Clasp_202396-1507_1x15-1MP_P1.00mm_Horizontal
P1, P2, P3, P4: Plug; PinHeader_1x01_P2.00mm_Vertical
R1: 100; RESC1508X55N
R2, R3, R4, R5, R10, R11, R12, R13: 1M; RESC1608X55N
R6, R7, R8, R9, R14, R15, R16, R17: 33; RESC1608X55N
R18: 1.5k; RESC1608X55N
R19: 120; RES_ERA3AEB121V
U1: DSC1001AI2-032.7680; DFN4_7X5_MCH
U2: AD7768-4BSTZ; QFP50P1200X1200X160-64N
U3, U4, U5, U6: RM_8_ADI; ADA4841-2YRMZ
U7: THVD8000DDFR; SOT-23-8_Handsoldering
U8: ADP7118ARDZ-3.3-R7; SOIC_08_EP_3P9X4P9_ADI
U9: ADR435BRZ; ADI-R-8_M
U10: REG103UA-5; D0008A_M
U11: ADR4540BRZ; ADI-R-8_M

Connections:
3.3MCU: J1.1, U7.8 (VCC)
5V: 5V1.1, C6.2, C7.2, C8.2, C9.2, C10.1, C11.1, C12.1, C13.1, C14.1, C15.1, C16.1, C17.1, C24.1, C25.1, C26.1, C27.1, C37.2, C38.1, J3.2, U2.4 (AVDD1A), U2.45 (AVDD1B), U2.53 (AVDD2B), U2.60 (AVDD2A), U3.8 (+VS), U4.8 (+VS), U5.8 (+VS), U6.8 (+VS), U8.5 (EN), U8.7 (VIN), U8.8 (VIN), U10.1 (VOUT), U10.2 (VOUT), U11.2 (VIN)
5V ref: 5Vref1.1, C39.1, J4.1, J4.3, J4.5, J4.7, U9.6 (VOUT)
12V: J3.1, U9.2 (VIN), U10.5 (EN), U10.7 (VIN), U10.8 (VIN)
A: C34.2, J3.5, J3.6
AIN0+: C18.2, C22.1, R6.2, U2.64 (AIN0+)
AIN0-: C19.1, C22.2, R7.2, U2.63 (AIN0-)
AIN1+: C20.2, C23.1, R8.2, U2.2 (AIN1+)
AIN1-: C21.1, C23.2, R9.2, U2.1 (AIN1-)
AIN2+: C28.2, C32.1, R14.2, U2.49 (AIN2+)
AIN2-: C29.1, C32.2, R15.2, U2.50 (AIN2-)
AIN3+: C30.2, C33.1, R16.2, U2.47 (AIN3+)
AIN3-: C31.1, C33.2, R17.2, U2.48 (AIN3-)
B: C35.2, J3.3, J3.4
CS: J2.10, U2.16 (ST0/!CS)
DCLK: J2.2, U2.28 (DCLK)
DOUT0: J2.3, U2.27 (DOUT0)
DOUT1: J2.4, U2.26 (DOUT1)
DOUT2: J2.5, U2.25 (DOUT2)
DOUT3: J2.6, U2.24 (DOUT3)
DRDY: J2.1, U2.29 (~DRDY\)
GND: C1.1, C2.2, C3.1, C4.1, C5.1, C6.1, C7.1, C8.1, C9.1, C10.2, C11.2, C12.2, C13.2, C14.2, C15.2, C16.2, C17.2, C18.1, C19.2, C20.1, C21.2, C24.2, C25.2, C26.2, C27.2, C28.1, C29.2, C30.1, C31.2, C36.2, C37.1, C38.2, C39.2, C40.1, C41.2, J3.7, J4.2, J4.4, J4.6, P1.1, P2.1, P3.1, R1.2, R2.1, R3.1, R4.1, R5.1, R10.1, R11.1, R12.2, R13.2, R18.1, U1.2 (GND), U1.5 (EPAD), U2.3 (AVSS1A), U2.5 (REF1-), U2.7 (AVSS), U2.8 (AVSS), U2.9 (AVSS), U2.10 (AVSS), U2.31 (XTAL1), U2.33 (DGND), U2.39 (AVSS), U2.40 (AVSS), U2.41 (AVSS), U2.42 (AVSS), U2.44 (REF2-), U2.46 (AVSS1B), U2.51 (AVSS2B), U2.54 (AVSS), U2.55 (DGND), U2.56 (FORMAT0), U2.58 (CLK_SEL), U2.62 (AVSS2A), U3.4 (-VS), U4.4 (-VS), U5.4 (-VS), U6.4 (-VS), U7.5 (GND), U8.4 (GND), U8.EPAD, U9.4 (GND), U10.4 (GND), U11.4 (GND)
IN0+: J4.13, R2.2, U3.3 (+IN1)
IN0-: J4.12, R3.2, U3.5 (+IN2)
IN1+: J4.15, R4.2, U4.3 (+IN1)
IN1-: J4.14, R5.2, U4.5 (+IN2)
IN2+: J4.10, R12.1, U6.3 (+IN1)
IN2-: J4.11, R13.1, U6.5 (+IN2)
IN3+: J4.8, R10.2, U5.3 (+IN1)
IN3-: J4.9, R11.2, U5.5 (+IN2)
MODE: J1.3, U7.2 (MODE)
unnamed: C3.2, U2.34 (DREGCAP)
unnamed: C4.2, U2.61 (REGCAPA)
unnamed: C5.2, U2.52 (REGCAPB)
unnamed: C34.1, R19.1, U7.6 (A)
unnamed: C35.1, R19.2, U7.7 (B)
unnamed: R1.1, U2.21 (DIN)
unnamed: R6.1, U3.1 (OUT1), U3.2 (-IN1)
unnamed: R7.1, U3.6 (-IN2), U3.7 (OUT2)
unnamed: R8.1, U4.1 (OUT1), U4.2 (-IN1)
unnamed: R9.1, U4.6 (-IN2), U4.7 (OUT2)
unnamed: R14.1, U6.1 (OUT1), U6.2 (-IN1)
unnamed: R15.1, U6.6 (-IN2), U6.7 (OUT2)
unnamed: R16.1, U5.1 (OUT1), U5.2 (-IN1)
unnamed: R17.1, U5.6 (-IN2), U5.7 (OUT2)
unnamed: R18.2, U7.3 (F_SET)
unnamed: U1.3 (OUT), U2.32 (XTAL2/MCLK)
RS485RX: J1.2, U7.1 (R)
RS485TX: J1.4, U7.4 (D)
SCLK: J2.9, U2.17 (SCLK)
SDI: J2.8, U2.18 (DEC1/SDI)
SDO: J2.7, U2.19 (DEC0/SDO)
SYNC: U2.36 (~SYNC_IN\), U2.38 (~SYNC_OUT\)
V3ref: C36.1, U1.1 (*STANDBY), U1.4 (VDD), U2.11 (FILTER/GPIO4), U2.30 (~RESET\), U2.35 (IOVDD), U2.57 (~PIN!/SPI\), U8.1 (VOUT), U8.2 (VOUT), U8.3 (SENSE/ADJ)
V4ref: C1.2, C2.1, C40.2, C41.1, U2.6 (REF1+), U2.43 (REF2+), U11.6 (VOUT)
VCM: P4.1, U2.59 (VCM)

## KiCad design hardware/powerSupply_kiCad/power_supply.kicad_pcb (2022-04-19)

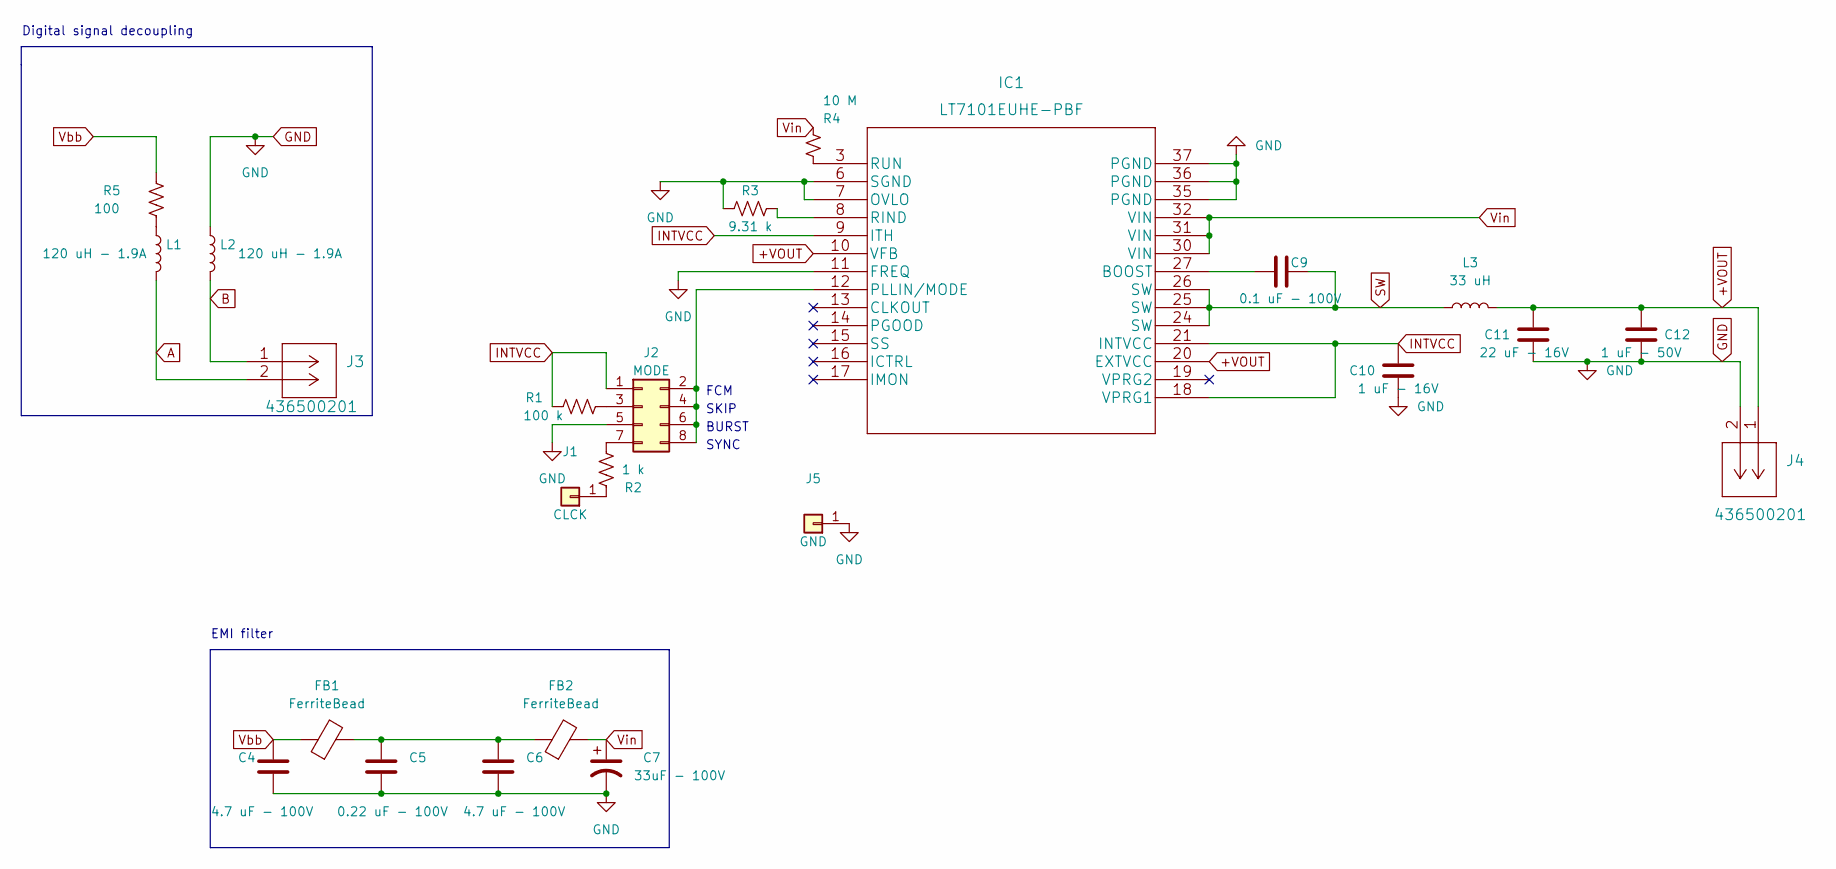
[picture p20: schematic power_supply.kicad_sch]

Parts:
C4, C6: 4.7 uF - 100V; C_1210_3225Metric
C5: 0.22 uF - 100V; C_0805_2012Metric
C7: 33uF - 100V; CP_Elec_10x10.5
C9: 0.1 uF - 100V; C_0805_2012Metric
C10: 1 uF - 16V; C_0805_2012Metric
C11: 22 uF - 16V; C_1210_3225Metric
C12: 1 uF - 50V; C_0805_2012Metric
FB1, FB2: FerriteBead; C_0805_2012Metric
IC1: LT7101EUHE-PBF
J1: CLCK; PinHeader_1x01_P2.54mm_Vertical
J2: MODE; PinHeader_2x04_P2.54mm_Vertical
J3, J4: 436500201
J5: GND; PinHeader_1x01_P2.54mm_Vertical
L1, L2: 120 uH - 1.9A; INDPM120120X805N
L3: 33 uH; SPM7054VT
R1: 100 k; R_0603_1608Metric
R2: 1 k; R_0603_1608Metric
R3: 9.31 k; R_0603_1608Metric
R4: 10 M; R_0805_2012Metric
R5: 100; TO-220-2_Vertical

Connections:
+VOUT: C11.1, C12.1, IC1.10 (VFB), IC1.20 (EXTVCC), J4.1, L3.2
A: J3.2, L1.2
B: J3.1, L2.2
GND: C4.2, C5.2, C6.2, C7.2, C10.2, C11.2, C12.2, IC1.6 (SGND), IC1.7 (OVLO), IC1.11 (FREQ), IC1.35 (PGND), IC1.36 (PGND), IC1.37 (PGND), J2.5, J4.2, J5.1, L2.1, R3.1
INTVCC: C10.1, IC1.9 (ITH), IC1.18 (VPRG1), IC1.21 (INTVCC), J2.1, R1.1
unnamed: C5.1, C6.1, FB1.2, FB2.1
unnamed: C9.1, IC1.27 (BOOST)
unnamed: IC1.3 (RUN), R4.2
unnamed: IC1.8 (RIND), R3.2
unnamed: IC1.12 (PLLIN/MODE), J2.2, J2.4, J2.6, J2.8
unnamed: J1.1, R2.1
unnamed: J2.3, R1.2
unnamed: J2.7, R2.2
unnamed: L1.1, R5.2
SW: C9.2, IC1.24 (SW), IC1.25 (SW), IC1.26 (SW), L3.1
Vbb: C4.1, FB1.1, R5.1
Vin: C7.1, FB2.2, IC1.30 (VIN), IC1.31 (VIN), IC1.32 (VIN), R4.1

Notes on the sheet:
BURST
FCM
SKIP
EMI filter
SYNC
Digital signal decoupling

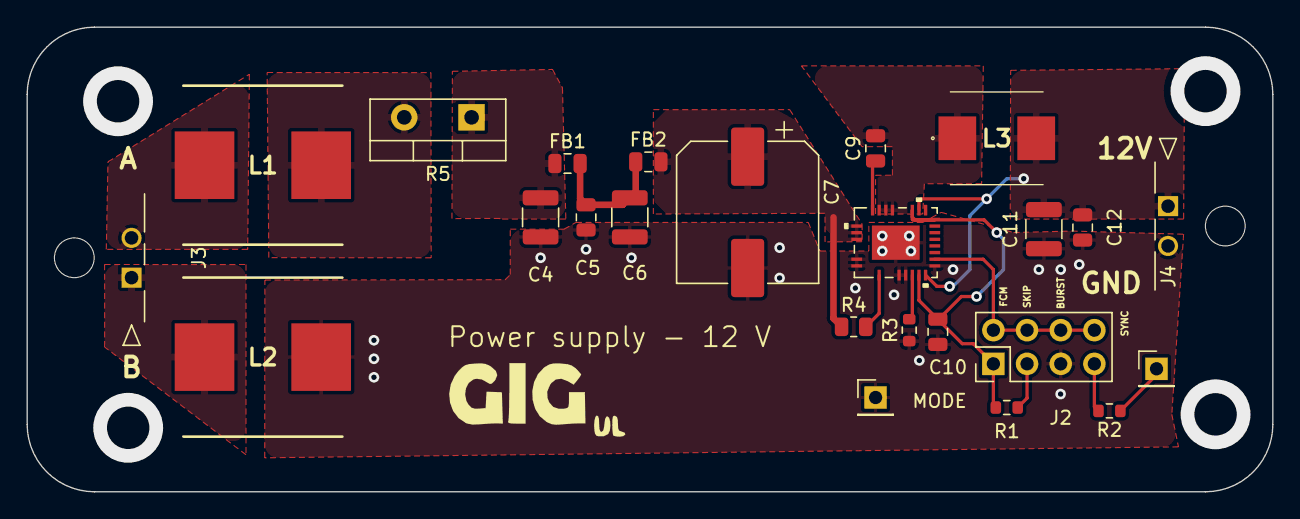
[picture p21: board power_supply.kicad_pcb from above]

Board: 2 copper layers, 94.0 x 35.1 mm, 24 parts (0 on the bottom side), 17 nets.

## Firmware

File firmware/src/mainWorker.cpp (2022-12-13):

#include <Arduino.h>
#include <ad7768.h> 
#include <command.h>
#include <stdio.h>
#include <cmath>
#include <SPI.h>
#include <Vector.h>
#include <string>
#include <elapsedMillis.h>



#define RS485Serial Serial3

int Mode = 9; // high = send = D2 led off, low = listen = D2 led high
command receivedCommand; 
int ODR;
int numberOfByte = 32;
int duration;
int samplingRate;
bool mustSendStatus = false;
bool mustSendData = false;
bool readyToTrig = false;
int workerStatus = IDLE;
int workerID = 1;
int chipSelectPin = 10;
ad7768_chip _default = {
		/* Configuration */
		.chipSelectPin = chipSelectPin,
		.power_mode = AD7768_ECO,
		.mclk_div = AD7768_MCLK_DIV_32,
		.dclk_div = AD7768_DCLK_DIV_8,
		.dec_rate = AD7768_DEC_X1024,
		.filt_type = AD7768_FILTER_SINC,

	};
ad7768_chip _seismic = {
		/* Configuration */
		.chipSelectPin = chipSelectPin,
		.power_mode = AD7768_ECO,
		.mclk_div = AD7768_MCLK_DIV_32,
		.dclk_div = AD7768_DCLK_DIV_8,
		.dec_rate = AD7768_DEC_X32,
		.filt_type = AD7768_FILTER_SINC,

	};
ad7768_chip configType = _seismic;

// pin declaration
int dout0 = 2;
int dout1 = 3;
int dout2 = 4;
int clck = 6;
int drdy = 18;
#define encoderA 20
#define encoderB 19
int cs = 16;
int IN1 = 7;
int IN2 = 8;

volatile long countA = 0.0;
float nbrpoles = 12.0;
float nbrToursMoteur;
float nbrToursArbre; 
float division_factor = 0.00322 * 837.76; 
elapsedMillis taskTimer = 0;
unsigned int taskDelay = 100; //ms
volatile int current = 0;
volatile int current_limit = 760; //mA
volatile int current_average_factor = 1000;
volatile int number_of_averaging_loop = current_average_factor / 20;
volatile int current_number_of_averaging_loop = 0;
volatile int avg = 0;
int pwm = 240;
int direction = 0; // 0 == IDLE, 1 == FORWARD, -1 == BACKWARD
int coastingTime = 500; //ms


void pulseA();     
void coast(int time);
void currentSense();


// ISR functions
void read_ISR();
void drdy_ISR();

// binary_data-ready flags and counter
volatile bool data_packet_ready = false;
volatile int acquisition_initial_time;
volatile int data_packet_counter = 0; 


// trigger state
volatile bool init_trig_detected = false;
volatile bool triggered_state = false;

// clock count for each binary_data packet
volatile int clck_count = 0;

// binary_data buffer and precalculated 2s power
volatile int expo [32] = {0,0,0,0,0,0,0,0,pow(2,23),pow(2,22),pow(2,21),pow(2,20),
pow(2,19),pow(2,18),pow(2,17),pow(2,16),pow(2,15),pow(2,14),
pow(2,13),pow(2,12),pow(2,11),pow(2,10),pow(2,9),pow(2,8),pow(2,7),pow(2,6),pow(2,5),
pow(2,4),pow(2,3),pow(2,2),pow(2,1),pow(2,0)};
volatile int binary_data0[32];
volatile double integer_data0 = 0;

volatile int binary_data1[32];
volatile double integer_data1 = 0;

volatile int binary_data2[32];
volatile double integer_data2 = 0;




int number_of_data_packet =1600;

// vector that holds a complete acquisition
int storage_arrayD0[16000]; //TODO: This maximum array size is 0.5 sec for 32 khz ODR
int storage_arrayT0[16000];
Vector<int> data0(storage_arrayD0);
Vector<int> time(storage_arrayT0);

int storage_arrayD1[16000]; //TODO: This maximum array size is 0.5 sec for 32 khz ODR
// int storage_arrayT1[32000];
Vector<int> data1(storage_arrayD1);
// Vector<int> time0(storage_arrayT1);

int storage_arrayD2[16000]; //TODO: This maximum array size is 0.5 sec for 32 khz ODR
// int storage_arrayT2[32000];
Vector<int> data2(storage_arrayD2);
// Vector<int> time(storage_arrayT2);

// When the lenght of the array is 32k the memory is overflowing.

void setup() {

  RS485Serial.begin(115200);
  Serial.begin(115200);   
  pinMode(Mode,OUTPUT);
  digitalWrite(Mode,LOW);
  SPI.begin();
  pinMode(dout0, INPUT);
  pinMode(drdy, INPUT_PULLDOWN);
  pinMode(clck, INPUT);
  pinMode(chipSelectPin, OUTPUT);
  pinMode(cs, INPUT);
  pinMode(IN1, OUTPUT);
  pinMode(IN2, OUTPUT);
  pinMode(encoderA, INPUT);
  pinMode(encoderB, INPUT);

  delay(100);
  ad7768_setup(configType);
}

void loop() {

if(RS485Serial.available () >0 and readyToTrig == false) 
{
  // String test;

  receivedCommand = readCommand(&RS485Serial);
  // Serial.println(receivedCommand.def);
  // Serial.println(receivedCommand.workerId);
  // test = RS485Serial.readStringUntil('\n');
  // Serial.println(test);
  if (receivedCommand.type == GLOBAL or receivedCommand.workerId == workerID)
  {
    // Serial.println("called");
    // Serial.println(receivedCommand.def);
    // Serial.println(receivedCommand.workerId);

  if (receivedCommand.def == ARM)
  {
    workerStatus = ARMED;
    Serial.println("armed");
    data_packet_counter = 0;
    readyToTrig = true;

    attachInterrupt(digitalPinToInterrupt(drdy), drdy_ISR, RISING);
    attachInterrupt(digitalPinToInterrupt(clck), read_ISR, FALLING);
  }
  else if (receivedCommand.def == STATUS)
  {
    digitalWrite(Mode,HIGH);
    delay(5);
    sendWorkerStatus(&RS485Serial,workerStatus,workerID);
    delay(5);
    digitalWrite(Mode,LOW);
    delay(5);
  }
  else if (receivedCommand.def == CONFIG)
   {
    //  Serial.print(receivedCommand.adcConfig);
     Serial.print("config");
     if (receivedCommand.adcConfig == DEFAULT)
     {configType = _default;}
     else if (receivedCommand.adcConfig == SEISMIC)
     {configType = _seismic;} 
     int index = receivedCommand.data.indexOf("T");   
     samplingRate = receivedCommand.data.substring(0,index).toInt();
     duration = receivedCommand.data.substring(index+1).toInt();
    if (samplingRate == 32)
     {
      configType.dec_rate = AD7768_DEC_X32;
      }
    else if (samplingRate == 16)
      {
      configType.dec_rate = AD7768_DEC_X64;
      }
    else if (samplingRate == 8)
      {
      configType.dec_rate = AD7768_DEC_X128;
      }
    else if (samplingRate == 4)
      {
      configType.dec_rate = AD7768_DEC_X256;
      }
    else if (samplingRate == 2)
      {
      configType.dec_rate = AD7768_DEC_X512;
      }
    else if (samplingRate == 1)
      {
      configType.dec_rate = AD7768_DEC_X1024;
      }

     ad7768_setup(configType);
     workerStatus = CONFIGURED;

    // delay(5);
    // digitalWrite(Mode,HIGH);
    // delay(5);
    // sendWorkerStatus(&RS485Serial,workerStatus,workerID);
    // delay(5);
    // digitalWrite(Mode,LOW);


    number_of_data_packet =  int(((duration/1000.0) * (samplingRate*1000.0)));
    // delay(5);
    // digitalWrite(Mode,HIGH);
    // delay(5);



    // RS485Serial.println(number_of_data_packet);

    // RS485Serial.println(receivedCommand.data);
    // RS485Serial.println(receivedCommand.data.substring(index+1).toInt());
    // ODR = print_config(configType, &RS485Serial);
    // RS485Serial.flush();
    // delay(5);
    // RS485Serial.print(duration);RS485Serial.println(samplingRate);
    //     delay(5);

    // RS485Serial.println('s');
    // digitalWrite(Mode,LOW);

 
    // Serial.println(number_of_data_packet);
    // workerStatus = IDLE;
    

   }
  else if (receivedCommand.def == HARVEST)
  {
    mustSendData = true;
    Serial.println("called for harvest");
  }
  else if (receivedCommand.def == MOTOR)
  {
    String direction = receivedCommand.data;
   if (direction == "forward")
   {
    current = 0;
    coast(coastingTime);
    analogWrite(IN1, pwm);
    analogWrite(IN2, 0);
    delay(1000);
    
    attachInterrupt(digitalPinToInterrupt(encoderA), pulseA, RISING);

    while (current < current_limit)
    {
    analogWrite(IN1, pwm);
    analogWrite(IN2, 0);
    
    nbrToursMoteur = countA/nbrpoles; //Diviser par le nombre de pole pour obtenir le vrai rpm du moteur
    nbrToursArbre = nbrToursMoteur/721.0 ;  // Appliquer le ratio du réducteur
    
    if (taskTimer > taskDelay )
  {
    digitalWrite(Mode,HIGH);
  
    RS485Serial.print(current);RS485Serial.print(",");
    
    RS485Serial.println(nbrToursArbre);
    digitalWrite(Mode,LOW);
    taskTimer = 0;

  }
  
  
    }
    coast(coastingTime);
        
    digitalWrite(Mode,HIGH);
    RS485Serial.println('w');
    RS485Serial.print('T');
    RS485Serial.println(nbrToursArbre);
    RS485Serial.print('S');RS485Serial.println(current);
    delay(5);
    digitalWrite(Mode,LOW);
  }
   
   if (direction == "backward")
   {
    current = 0;
    coast(coastingTime);
    analogWrite(IN1, 0);
    analogWrite(IN2, pwm);
    delay(1000);

    attachInterrupt(digitalPinToInterrupt(encoderA), pulseA, RISING);

    while (current < current_limit)
    {
    analogWrite(IN1, 0);
    analogWrite(IN2, pwm);
    
    nbrToursMoteur = countA/nbrpoles; //Diviser par le nombre de pole pour obtenir le vrai rpm du moteur
    nbrToursArbre = nbrToursMoteur/721.0 ;  // Appliquer le ratio du réducteur
    
    if (taskTimer > taskDelay )
  {
    digitalWrite(Mode,HIGH);
  
    RS485Serial.print(current);RS485Serial.print(",");
    
    RS485Serial.println(nbrToursArbre);
    digitalWrite(Mode,LOW);
    taskTimer = 0;

  }
  
  
    }
    coast(coastingTime);
        
    
    digitalWrite(Mode,HIGH);
    RS485Serial.println('w');
    RS485Serial.print('T');
    RS485Serial.println(nbrToursArbre);
    RS485Serial.print('S');RS485Serial.println(current);
    delay(5);
    digitalWrite(Mode,LOW);
   }
   
   if (direction == "stop")
   {
    coast(coastingTime);
   }
   }
   
  }
  
  }

   

  if (mustSendData == true)
  {
    digitalWrite(Mode,HIGH);
     delay(5);
    RS485Serial.print(workerID);RS485Serial.println('w');
    delay(5);
    RS485Serial.print(number_of_data_packet);RS485Serial.println(':');
    delay(5);
    for (int i = 0; i < number_of_data_packet; i++)
      {
        RS485Serial.print(time.at(i));RS485Serial.print(",");
        RS485Serial.print(data0.at(i));RS485Serial.print(",");
        RS485Serial.print(data1.at(i));RS485Serial.print(",");
        RS485Serial.print(data2.at(i));
        RS485Serial.print(':');
        delay(1);
      }
    RS485Serial.flush();
    digitalWrite(Mode,LOW);
    mustSendData = false;
    workerStatus = IDLE;
    time.clear();
    data0.clear();
    data1.clear();
    data2.clear();
  }


noInterrupts();
if (readyToTrig == true and triggered_state == false)
{
 if (RS485Serial.find('t'))
{
    acquisition_initial_time = micros();
    triggered_state = true;
  }
}
if (data_packet_ready == true and triggered_state == true)
{		

    data0.push_back(integer_data0);
    data1.push_back(integer_data1);
    data2.push_back(integer_data2);
    time.push_back(micros() - acquisition_initial_time);

		data_packet_ready = false;
		data_packet_counter += 1;

		if (data_packet_counter == number_of_data_packet)
		{
      workerStatus = DATAREADY;
      // mustSendStatus = true;
			triggered_state = false;
      readyToTrig = false;
      data_packet_counter = 0;
      detachInterrupt(digitalPinToInterrupt(drdy));
      detachInterrupt(digitalPinToInterrupt(clck));
		}

}
interrupts();
}

void read_ISR() {
if (clck_count < 32){ // because the output is 32 bit long
// delayNanoseconds(10);
binary_data0[clck_count] = digitalRead(dout0);
binary_data1[clck_count] = digitalReadFast(dout1);
binary_data2[clck_count] = digitalReadFast(dout2);
clck_count += 1;


}
else if (clck_count == 33){ // directly after the last bit
	data_packet_ready = true;
	for (int i = 8; i < 32; i++) { // data bit is from 8 to 32
      integer_data0 +=  expo[i] * binary_data0[i];
			integer_data1 +=  expo[i] * binary_data1[i];
      integer_data2 +=  expo[i] * binary_data2[i];

			}
	clck_count += 1;

}

else {
	clck_count += 1;
}
}

void drdy_ISR(){
	if (triggered_state == true)
	{
	clck_count = 0;
	integer_data0 = 0;	
  integer_data1 = 0;	
  integer_data2 = 0;	
	}
	

}
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

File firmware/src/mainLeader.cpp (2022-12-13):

#include <Arduino.h>
#include <ad7768.h>
#include <command.h>

#define RS485Serial Serial3

//TODO: Print instructions

int Mode = 9; // high = send = D2 led off, low = listen = D2 led high
int trig = 22;
String instruction;
bool waitingForworkerResponse = false;
bool waitForData = false;
bool waitForMotorState = false;
int number_of_data_packet;
String duration = "50";
String sampling_rate = "32";

void trig_ISR();

volatile bool init_trig_detected = false;
volatile bool triggered_state = false;

void setup() {
  RS485Serial.begin(115200);
  Serial.begin(115200);
  pinMode(Mode,OUTPUT);
  digitalWrite(Mode,LOW);
  pinMode(trig,INPUT_PULLDOWN);
}

void loop() {

if (Serial.available() ) 
  {
    instruction = Serial.readStringUntil('\n');
    instruction.trim();
     // I always want the status of the worker after a command
    String temp;
    temp = instruction.substring(instruction.length() - 1);
    int workerid = temp.toInt();

	if (instruction.equals("arm")) {
    digitalWrite(Mode,HIGH);
    delay(5);
    arm(&RS485Serial);
    delay(5);
    digitalWrite(Mode,LOW);
    Serial.println("arming...");
    Serial.flush();
    attachInterrupt(digitalPinToInterrupt(trig),trig_ISR,LOW);
    // waitingForworkerResponse = true;

  }
  if (instruction.equals("background")){
    digitalWrite(Mode,HIGH);
    delay(5);
    arm(&RS485Serial);
    delay(5);
    digitalWrite(Mode,LOW);
    Serial.println("arming...");
    Serial.flush();
    triggered_state = true;
  }
  if (instruction.startsWith("get status")) {
    digitalWrite(Mode,HIGH);
    delay(5);
    getWorkerStatus(&RS485Serial,workerid);
    delay(5);
    digitalWrite(Mode,LOW);
  }
  if (instruction.startsWith("config acq")) {
    Serial.print("Configuration in process to : ");Serial.println(workerid);
    sampling_rate = Serial.readStringUntil('\n');
    duration = Serial.readStringUntil('\n');
    // Serial.println(sampling_rate);
    // Serial.println(duration);
    digitalWrite(Mode,HIGH);
    delay(5);
    sendConfigToADC(&RS485Serial,DEFAULT, sampling_rate + "T" + duration,workerid);
    delay(5);
    digitalWrite(Mode,LOW);
    delay(5);
    digitalWrite(Mode,HIGH);
    delay(5);
    getWorkerStatus(&RS485Serial,workerid);
    delay(5);
    digitalWrite(Mode,LOW);
    waitingForworkerResponse = true;
  }
  if (instruction.startsWith("config default")) {
    Serial.print("Configuration in process to : ");Serial.println(workerid);
    digitalWrite(Mode,HIGH);
    delay(5);
    sendConfigToADC(&RS485Serial,DEFAULT, duration,workerid);
    delay(5);
    digitalWrite(Mode,LOW);
    delay(5);
    // digitalWrite(Mode,HIGH);
    // delay(5);
    // getWorkerStatus(&RS485Serial,workerid);
    // delay(5);
    // digitalWrite(Mode,LOW);
    waitingForworkerResponse = true;
  }
  if (instruction.startsWith("config seismic")) {
    Serial.print("Configuration in process to : ");Serial.println(workerid);
    digitalWrite(Mode,HIGH);
    delay(5);
    sendConfigToADC(&RS485Serial,SEISMIC, duration,workerid); 
    delay(5);
    digitalWrite(Mode,LOW);
    delay(5);
    // digitalWrite(Mode,HIGH);
    // delay(5);
    // getWorkerStatus(&RS485Serial,workerid);
    // delay(5);
    // digitalWrite(Mode,LOW);
    waitingForworkerResponse = true;
  }
  if (instruction.startsWith("harvest")) {
    digitalWrite(Mode,HIGH);
    delay(5);
    HarvestData(&RS485Serial,workerid);
    delay(5);
    digitalWrite(Mode,LOW);
    Serial.print(workerid);Serial.println("harvesting");
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

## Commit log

2021-11-11 upload of the ad7768_v1 board
    [12061A121JAT2A.PcbLib, 12061A121JAT2A.SchLib, 12065A331JAT2A.PcbLib, 12065A331JAT2A.SchLib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]
2021-11-16 removed the PCB and the 4 to 8 channel schematic
    [PCB.PcbDoc, ad7768.SchDoc, ad7768_testboard.PrjPcb, driver4-8.SchDoc]
2021-11-16 changed the pin for the AD7768-4
    [ad7768.SchDoc, ad7768_testboard.SCHLIB]
2021-11-16 Update ad7768.SchDoc
    Verification of all the pins of the AD7768-4 after the symbol change
    [ad7768.SchDoc]
2021-11-16 imported the teensy on the schematic
    [ad7768.SchDoc]
2021-11-17 Connected the teensy to the ADC port
    [ad7768.SchDoc]
2021-11-17 implemented the power circuit for the THVD8000
    [Vref.SchDoc, ad7768_testboard.PrjPcb, driver0-3.SchDoc, thvd8000.SchDoc]
2021-11-17 better placing of the components in THVD8000
    [thvd8000.SchDoc]
2021-11-18 renaming and added the switch for reset
    [12061A121JAT2A.PcbLib, 12061A121JAT2A.SchLib, 12065A331JAT2A.PcbLib, 12065A331JAT2A.SchLib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]
2021-11-19 Changed all the resistor for the 0603 footprint and low drift
    Added the resistors for the analog input
    [ERA-3AEB121V.PcbLib, ERA-3AEB121V.SchLib, MCT0603MD1000DP500.PcbLib, MCT0603MD1000DP500.SchLib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]
2021-11-19 added the bloxking capacitor
    [GRM31CR61E476ME44K.PcbLib, GRM32EC72A106KE05K.PcbLib, GRM32EC72A106KE05K.SchLib, thvd8000.SchDoc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]
2021-11-19 added decoupling capacitor for voltage from AB lines
    [GRM31CR61E476ME44K.PcbLib, thvd8000.SchDoc]
2021-11-19 changed all the 1uF capacitor from 1206 to 0603 footprint
    [ad7768.SchDoc, driver0-3.SchDoc, thvd8000.SchDoc, workerBoard.PrjPcb]
2021-11-19 Changed the 0.1uF capacitor from 1206 footprint to 0603
    [06033D104KAT2A.PcbLib, 06033D104KAT2A.SchLib, ad7768.SchDoc, driver0-3.SchDoc]
2021-11-19 changed the 120pF capacitor from 1206 to 0603
    [06035A121GAT2A.PcbLib, 06035A121GAT2A.SchLib, GRT188R61A106ME13D.PcbLib, GRT188R61A106ME13D.SchLib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]
2021-11-19 changed the 330pF capacitor from 1206 to 0603
    [06033A331GAT2A.PcbLib, 06033A331GAT2A.SchLib, driver0-3.SchDoc]
2021-11-22 annotation of new copmponents
    [TMR 6-7211WIR.PcbLib, TMR 6-7211WIR.SchLib, ad7768.SchDoc, driver0-3.SchDoc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]
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2021-11-25 Validation of the projects removing the errors
    [ad7768.SchDoc]
2021-11-25 created pcbDoc for main board and created the SI1521
    The 1521 part was created in the GIGUL workspace in the altium cloud and then published (released)
    [accel.SchDoc, ad7768.SchDoc, adc_RS485_teensy.PcbDoc]
2021-11-26 5V noclean for MCU and ADC
    [Vref.SchDoc, ad7768.SchDoc, workerBoard.PrjPcb]
2021-11-26 added 5V clean and No clean
    [Vref.SchDoc, accel.SchDoc, ad7768.SchDoc, driver0-3.SchDoc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]
2021-11-26 Added power_supply draft
    Added power supply draft and removed the Capacitor series from the THVD8000 board
    [power_supply.SchDoc, thvd8000.SchDoc]
2021-11-26 Finished the accel schematic, missing only the connector
    [Vref.SchDoc, accel.SchDoc]
2021-11-26 annotations of accel board
    [accel.SchDoc]
2021-11-26 trying to import only some schematic
    [accel.SchDoc, adc_RS485_teensy.PcbDoc]
2021-11-26 imported missing footprints
    [C1210X474KARACAUTO.PcbLib, C1210X474KARACAUTO.SchLib, GRM31CR61E476ME44K.PcbLib, ad7768.SchDoc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]
2021-11-27 added componenet to pcb file
    [ADC_RS_MCU.PcbDoc, accel.SchDoc, workerBoard.PrjPcb]
2021-11-29 uploaded components into the draft board
    [ADC_RS_MCU.PcbDoc, ADC_RS_MCU_draft.PcbDoc, workerBoard.PrjPcb]
2021-11-29 generated STEP file for board
    [ADC_RS_MCU_draft.PcbDoc, accel.SchDoc, accel_draft.PcbDoc, accel_draft.step]
2021-11-30 set the 4 layer PCB
    [ADC_RS_MCU.PcbDoc, ad7768.SchDoc, workerBoard.PrjPcb]
2021-11-30 annotate and reorganize in the driver adc order
    [ADC_RS_MCU.PcbDoc, Vref.SchDoc, accel.SchDoc, ad7768.SchDoc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]
2021-11-30 remove the headers in the driver schematics
    [ADC_RS_MCU.PcbDoc, ad7768.SchDoc, driver0-3.SchDoc, workerBoard.PrjPcb]
2021-11-30 added via types
    [ADC_RS_MCU.PcbDoc, driver0-3.SchDoc]
2021-12-01 Driver0-3 routing
    [ADC_RS_MCU.PcbDoc]
2021-12-01 Update capacitor from Vref
    [ADC_RS_MCU.PcbDoc, Vref.SchDoc, ad7768.SchDoc]
2021-12-01 routing of the Vref schematic
    Missing the 12V and 5vref connector
    [ADC_RS_MCU.PcbDoc]
2021-12-01 moved the decoupling capacitor of the driver to the bottom layer
    [ADC_RS_MCU.PcbDoc]
2021-12-01 rearrange the orientaiton of the ADC and the order of driver for more direct routing
    [ADC_RS_MCU.PcbDoc]
2021-12-01 notes in the md file
    [ADC_RS_MCU.PcbDoc]
2021-12-09 connected all the 5V, 4Vref, 3Vref and other GND pin of the ADC
    [ADC_RS_MCU.PcbDoc, Vref.SchDoc, ad7768.SchDoc]
2021-12-09 placed all the capacitor and resistor to decouple the ADC
    [ADC_RS_MCU.PcbDoc, ad7768.SchDoc]
2021-12-09 placement of the name of each component
    [ADC_RS_MCU.PcbDoc]
2021-12-09 finish routing of main components
    [ADC_RS_MCU.PcbDoc]
2021-12-09 placed the A and B line with space for connectors
    [ADC_RS_MCU.PcbDoc]
2021-12-09 run DRC and have 38 Un-Routed Net Constraint error
    everywhere there is via
    [ADC_RS_MCU.PcbDoc]
2021-12-10 solved the unrouted error for via to the GND and 5V plane
    Added to assign a net to the split plane : show the plane on the PCB, double click and assing the split plane to a net name
    [ADC_RS_MCU.PcbDoc]
2021-12-10 modified footprint of 2 capacitor type to remove some clearance error
    [ADC_RS_MCU.PcbDoc, ad7768.SchDoc, driver0-3.SchDoc, thvd8000.SchDoc]
2021-12-10 I have choosen the connector #1 but footprint missing
    The connector 16 pin has been added to the driver schematic but the 3D model and footprint is missing. All the links for the parts are in the onenote documents
    [ADC_RS_MCU.PcbDoc, driver0-3.SchDoc]
2021-12-13 imported and routed the connector from the main board to the accels
    [ADC_RS_MCU.PcbDoc, driver0-3.SchDoc]
2021-12-14 modify the shape and routed the accel board
    [accel.SchDoc, accel_draft.PcbDoc]
2021-12-14 integrated the ring connector for the A and B line
    [ADC_RS_MCU.PcbDoc, accel.SchDoc, accel_draft.PcbDoc]
2021-12-14 integrated the terminal for the 12V and GND from power supply board
    [ADC_RS_MCU.PcbDoc, ad7768.SchDoc]
2021-12-14 renaming and 3D model generation
    [accel.PcbDoc, accel_draft.PcbDoc]
2021-12-14 added m2 screw to 3D model
    [accel.PcbDoc]
2021-12-14 changed the alimention of the thvd8000 from the 3.3V to the 3.3MCU
    [ADC_RS_MCU.PcbDoc, accel.PcbDoc, ad7768.SchDoc, driver0-3.SchDoc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]
2021-12-15 changed the 3.3V ref voltage chip to match the current need
    Took the adp7118-3.3 as recommended in the adc datasheet
    [ADP7118ARDZ-3.3.PcbLib, Vref.SchDoc]
2021-12-15 modified the c3 and c8 footprint to satisfy design rule
    [ADC_RS_MCU.PcbDoc, Vref.SchDoc]
2021-12-17 changed the terminal (12V-GND) for m3 screw. Also changed the A-B to m3 screw
    [ADC_RS_MCU.PcbDoc, Vref.SchDoc, thvd8000.SchDoc]
2021-12-17 revision of the THVD8000 circuit and removal of the L1 and L2
    The L1 and L2 are going to be on the power supply instead
    [ADC_RS_MCU.PcbDoc, power_supply.SchDoc, thvd8000.SchDoc]
2021-12-20 reorganisation of the board to let more place for the screw connectors
    [ADC_RS_MCU.PcbDoc]
2021-12-20 added the BOM in the project output file
    [ADC_RS_MCU.PcbDoc]
2021-12-20 changednthe 5V ref for thw 8soic footprint instead of the 8 sop
    8sop BO
    [ADC_RS_MCU.PcbDoc, Vref.SchDoc, ad7768.SchDoc]
2021-12-20 added clearance to the screw holes and place for the USB connector
    [ADC_RS_MCU.PcbDoc, Vref.SchDoc, power_supply.SchDoc]
2021-12-20 changed the via to make sure they are through holes
    [ADC_RS_MCU.PcbDoc, power_supply.SchDoc, thvd8000.SchDoc]
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2022-01-12 adding clearance on different traces
    [ADC_RS_MCU.PcbDoc, accel.PcbDoc]
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2022-01-14 removed the clearance outline error
    [ADC_RS_MCU.PcbDoc]
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2022-01-17 moved the outline rectangle to mechanical layer 1
    The board outline error are now eliminated
    [ADC_RS_MCU.PcbDoc]
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2022-03-24 pushing workerBoard in kicad version
    Still some bugs:
    - Pad 4 and 8 of the op amp are not connected to the good net
    [ADC_RS_MCU.kicad_pcb, ADC_RS_MCU.kicad_sch, Vref.kicad_sch, ad7768.kicad_sch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]
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2022-03-29 Replace label in only 2 dimensions and without overlaping on traacks
    [ADC_RS_MCU.kicad_pcb]
2022-03-29 DRC clean
    Remove the warning by repositioning the label on both top and bottom layer
    Replace the +5V net for the 5V net
    [ADC_RS_MCU.kicad_pcb, ADC_RS_MCU.kicad_sch, driver0-3.kicad_sch]
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2022-07-29 Fixed DRC violations
    Fixed DRC violations based on missing footprints. Should review THVD8000 foot print as it had to be changed from 'missing' footprint import. This version passes all DRC checks. Net clearance was chan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
    [ADC_RS_MCU.kicad_pcb, ADC_RS_MCU.kicad_sch, Vref.kicad_sch, ad7768.kicad_sch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]
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2022-07-31 Replaced micro-via for through hole via
    [ADC_RS_MCU.kicad_pcb]
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

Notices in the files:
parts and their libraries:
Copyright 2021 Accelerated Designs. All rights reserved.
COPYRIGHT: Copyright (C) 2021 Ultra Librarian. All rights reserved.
